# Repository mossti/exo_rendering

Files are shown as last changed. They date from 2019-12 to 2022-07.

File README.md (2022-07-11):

# CABLE-DRIVEN SERIES ELASTIC ACTUATOR FOR UPPER-LIMB REHABILITATIVE EXOSKELETON
*You can see the demo video [here](https://www.youtube.com/watch?v=A_MqyhAG-6s)!*

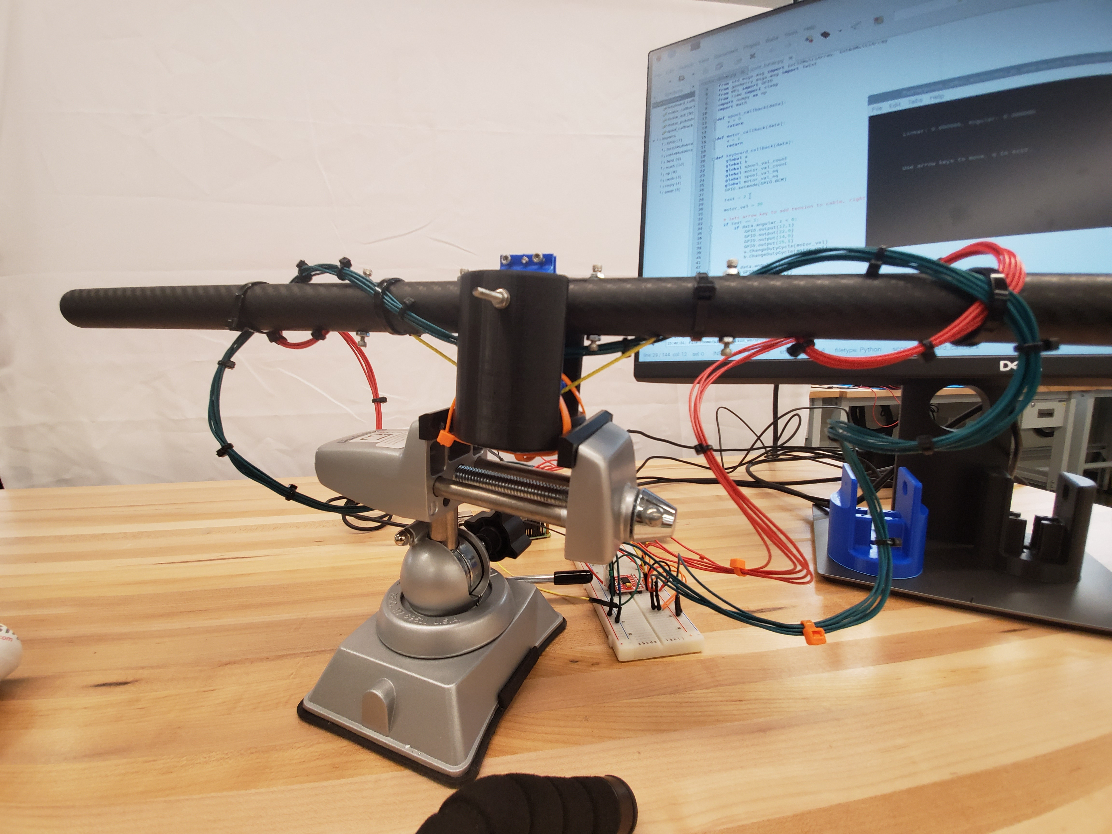
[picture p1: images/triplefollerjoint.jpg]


Individuals effected by a stroke will often develop symptomatic neuromotor control deficits. Depending on the degree of the stroke and the localization in the brain, these deficits can be categorized into impairments of specific neuromotor pathways. Reticulospinal (RS) hyperexcitability is currently believed to be the most likely candidate responsible for a common form of post-stroke spasticity, which can result in weakness and spasmodic motion control in the effected individual. In many cases, motor recovery and reduced spasticity can be achieved through rehabilitative therapy; historically this often takes form via hands-on manipulation and assistance by occupational therapists, repetitive goal-oriented intensive therapy, and medicinal treatments. These therapies, while effective, are often limited in scope by the availability and individual training of medical personnel, the cost of travel and therapy, and difficulties in customizing therapeutic approaches for individual patients.

Ideally, the design of a modular device to facilitate certain aspects common to motor recovery therapies would allow for a greater degree of accessibility to effected populations and more effective and regular training intervals (regularity of training periods is a key factor of successful neurorehabilitation). To this end, we propose a lightweight gravity-balancing exoskeleton with cable-driven elastic actuation, engineered to provide feedback which encourages synergistic patterns of movement that post-stroke spasticity commonly prohibits.

# DESCRIBE EXO; DESCRIBE AND SHOW SEA PROTOTYPES/COMPONENTS
A gravity-balancing machine (in this case, a gravity-balancing orthosis (GBO)) is defined as a mechanical system which can offload the force due to gravity (in part or whole) experienced by a load onto a separate component of the mechanism. In this device, the gravity-balancing subsystem is confined to the upper limbs, allowing for the downward force due to gravity to be offloaded via a series of counterweights (with specific degrees of freedom) onto the user's back. The device is engineered to assist with upper limb neuromotor rehabilitation, and--as such--is concentrated on the minimization of external forces on the upper limbs. Depending on the stage of recovery that a survivor of stroke is currently working through (and concordantly the severity of neuromuscular weakness), the reduction of gravitational forces can greatly reduce the effort/focus required by the user that is dedicated solely to counteracting gravity. Instead, the user's focus can be directed towards the repetitive goal-oriented therapy motions in a manner somewhat analogous to water immersive and equine therapy used for lower-limb rehabilitative approaches. Due to the positioning of the counterweights, the GBO can perform well for a wide range of arm configurations--and can certainly perform well within the range required for the user to engage in therapeutic tasks.

# EXO OVERVIEW
The GBO upper-limb exoskeleton is comprised of a consumer backpack frame (with waist strap for further weight distribution along the user's trunk), and a series of carbon fiber tubes (lightweight, high tensile strength).

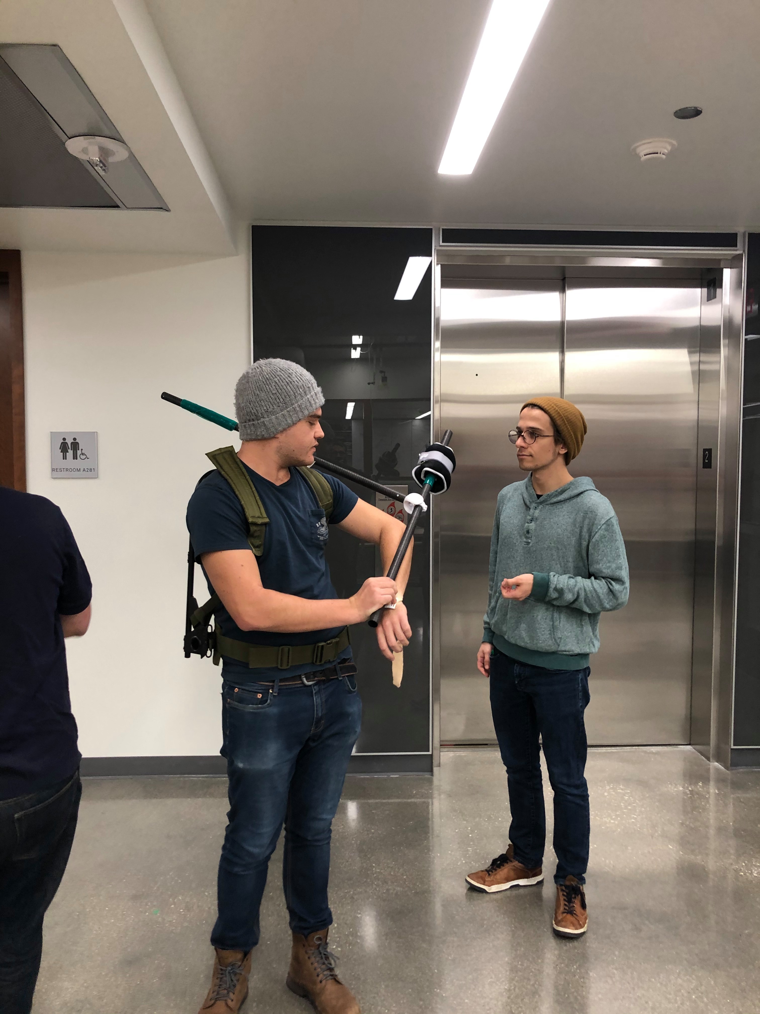
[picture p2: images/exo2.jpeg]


The weights can be adjusted to accommodate different arm lengths and musculature.

# SEA OVERVIEW
A series elastic actuator (SEA) is a form of actuator that inherently supports an elastic component between the actual actuator and the actuator's load. This boasts a number of helpful applications, especially in the domain of rehabilitative/assistive robotics. The elastic component allows for an otherwise rigid robotic system to interact with the environment around it (or a human element) in a non-rigid manner, providing 'give' to the joints. A wonderful caveatthat lends itself well to the realm of rehabilitative robotics is the ability to directly calculate the torque on a joint by tracking the difference in displacement of the motor and load on either side of the elastic component.

# SEA COMPONENTS

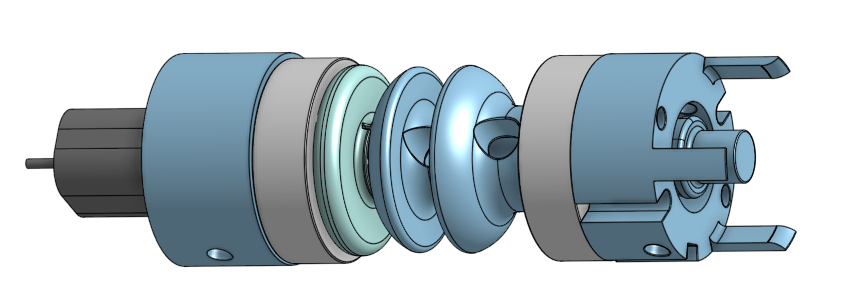
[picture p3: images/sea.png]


## BOM:

* Raspberry Pi 4 Model B (2GB RAM) x1
* Torsion Spring (360 deg, Left-Hand Wound, 0.174''OD) x2
* Ball Bearing (Open, Trade Number R2, for 1/8'' Shaft Diameter) x2
* Carbon Fiber Tube (1" OD, 15/16'' ID, 3ft) x1
* Dyneema Throw Line (MBS: 650lb) x1
* Dycem Non-Slip Material Roll x1
* SunFounder TB6612 H-Bridge x1
* Pololu 250:1 Micro Metal Gearmotor (HP 6V with Extended Motor Shaft) x2
* Pololu Magnetic Encoder Pair Kit for Micro Metal Gearmotors (12 CPR, 2.7-18V) x2
* AEAT-6012 Magnetic Encoder x2
* PLA and Ultimaker 2/3 (or equivalent)

NOTE: A large challenge in this mechanical design is that the assembly was required to fit within a 15/16in carbon fiber tube. Carbon fiber tubing is light, which makes it a strong candidate for exoskeleton scaffolding.

## Assembly

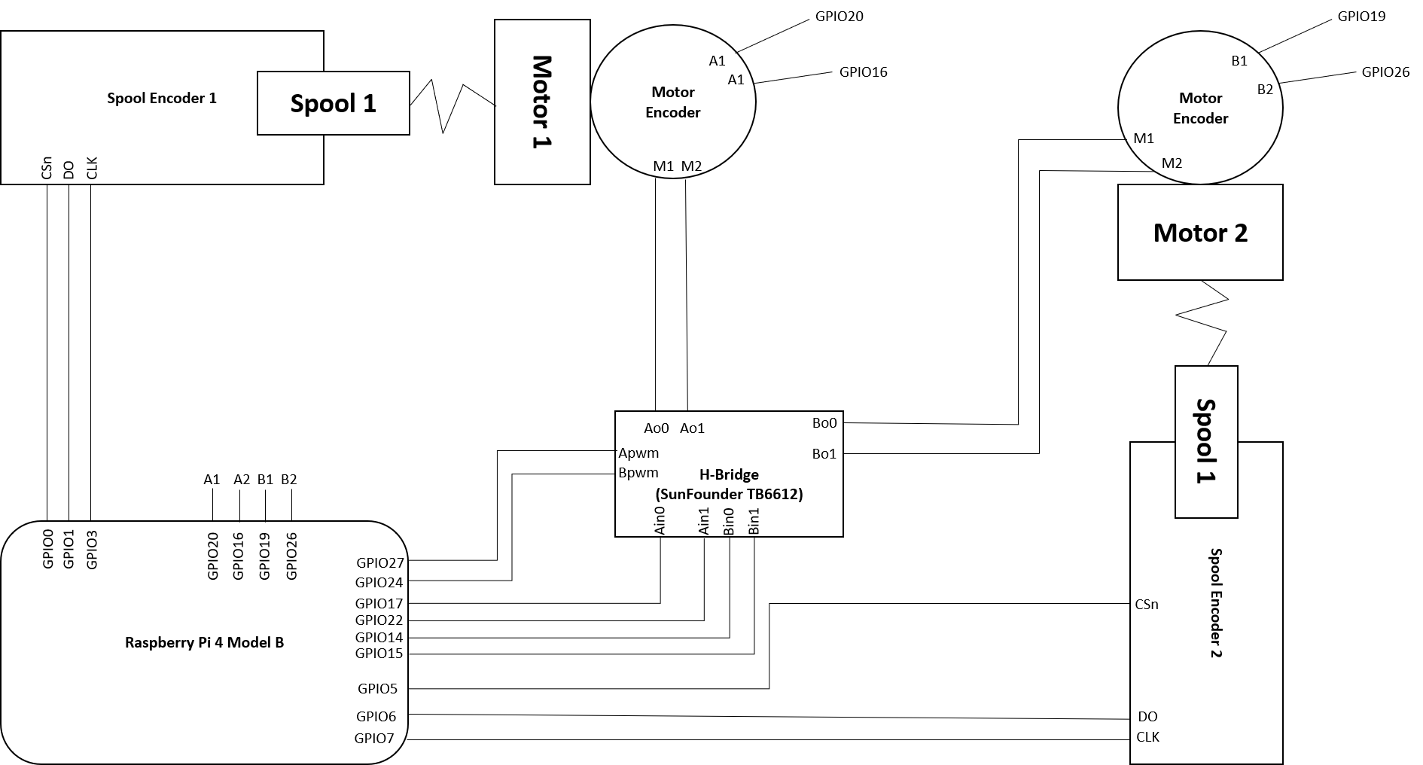
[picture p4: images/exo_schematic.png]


### Motors and motor encoders

The motor encoders are quadrature magnetic encoders attached to the back shaft of the MicroMetal gear motor with 6 counts per revolution (x250 due to gear ratio).

### Spool and spool encoders

The spool encoders are quadrature magnetic encoders with a max resolution of 4095 counters per revolution.

### Spring choice

The requirements for correcting small motions in the GBO are for a relatively low torque actuator that is back-driveable. To achieve this, 250:1 motors were used, connected to low spring constant torsion springs (K = 0.00536 Nm/rev) connected the motors to the spool (e.g., to the load).

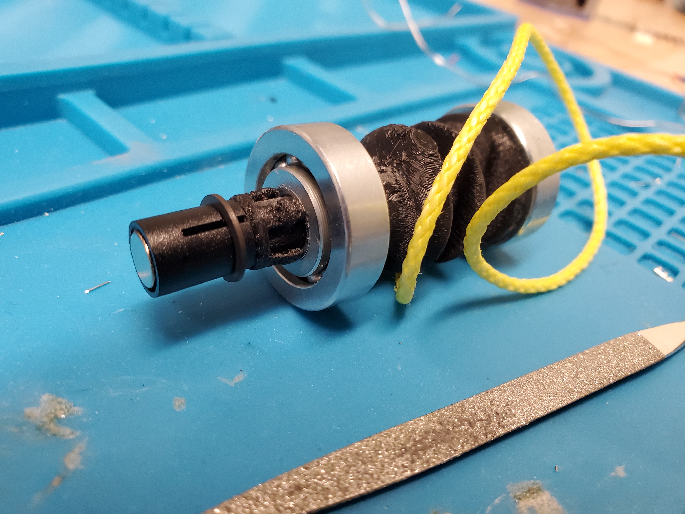
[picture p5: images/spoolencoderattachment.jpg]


# CODE

## ROS information and supporting packages:

This implementation uses:
* ROS Melodic
* catkin, geometry_msgs, roscpp, rospy, std_msgs
* teleop_tools package (for keyboard input tensioning) [get it here](https://github.com/ros-teleop/teleop_tools)!

To use this code, copy the `exo_joint` and the `teleop_tools` packages into your ROS workspace's src folder and run `catkin_make`.

## Pre-tensioning and cable actuation:

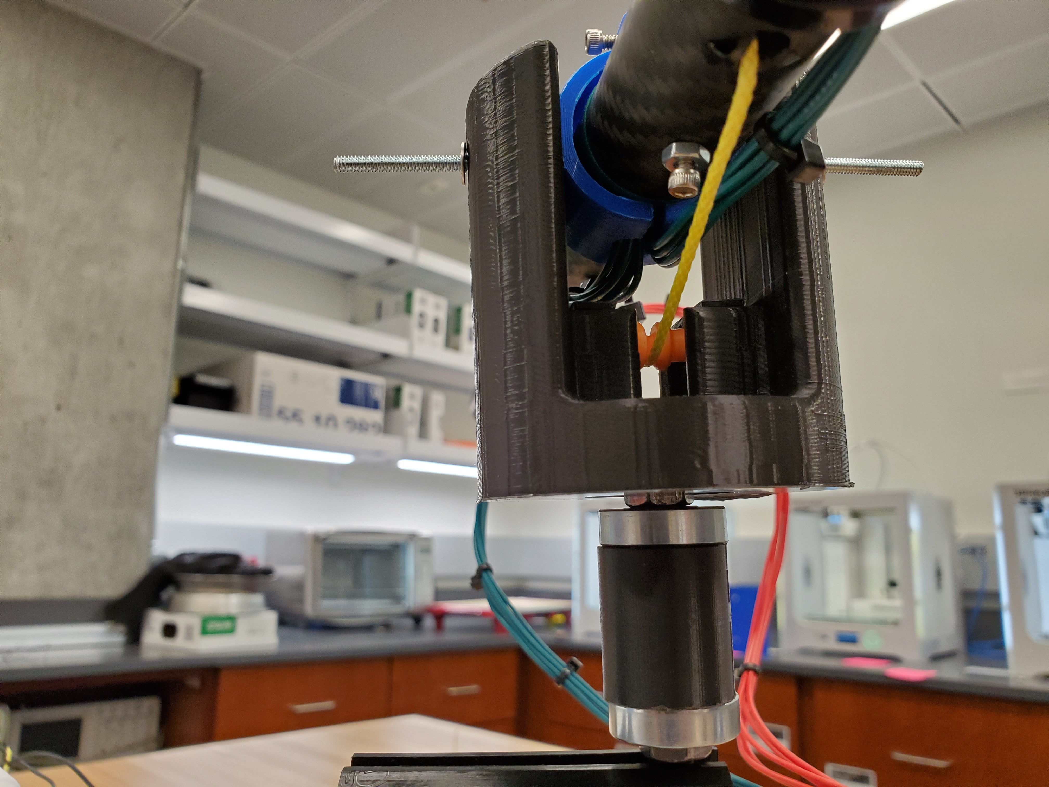
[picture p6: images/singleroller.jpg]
singleroller


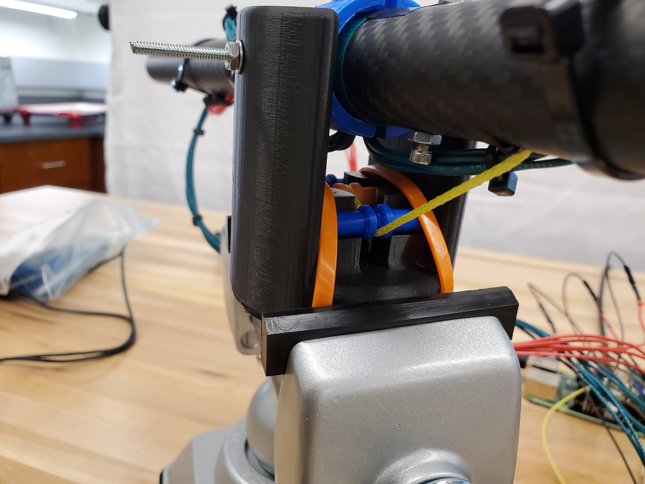
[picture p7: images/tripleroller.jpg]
doubleroller


To pre-tension, use `joint_tuner.py` via `roslaunch exo_joint joint_tuner.py`. Note that this will required `teleop_tools`.

Run `joint_tuner.launch` from the main ROS workspace directory and use the left (motor A CCW, motor B CW) and right (motor A CW, motor B CCW) arrow keys on your keyboard to manually adjust the tension and drive the cable.

## Prevent angular deflection:

The goal with this code (change `test = '1'` in `motor_driver.py`) is to correct small motions, such as those seen in post-stroke spasticity. When the spool encoder begins to increment outside of a threshold range (i.e., when torque is reached), the motor will pull on the spring in the opposite direction via a PID controller to bring the angle back to its original angle.

Run this with `roslaunch exo_joint angle_encoder_test.launch` after changing the value `test` in `motor_callback()` in `motor_driver.py` to `'1'`.

## Follow angular deflection:

The goal with this code (change `test = '2'` in `motor_driver.py`) is to achieve back-driveability. When the spool encoder increments (i.e., when there is sufficient torque on the spring, causing the spool to deflect), the motor fill follow it. This was done using a PID controller.

Run this with `roslaunch exo_joint angle_encoder_test.launch` after changing the value `test` in `motor_callback()` in `motor_driver.py` to `'2'`.

# FUTURE CONSIDERATIONS

One of the largest issues faced was the pre-tensioning of the cable drive. The cable used (Dyneema 650lb throw-line) is extremely low-friction, and using a single roller at ~35 degrees deflection was not enough to cause sufficient tension in the device. Tension is important because it is proportional to the amount of torque across the elastic component at any given time. Low tension means that the spool and motor encoders will behave less like an SEA and more like a conventional actuator with lag. The inclusion of three rollers helped, increasing the tension. This is visible in the demo video.

# CITATIONS

* [1] Agarwal, Priyanshu & Deshpande, Ashish. (2017). Series Elastic Actuators (SEAs) for Small-scale Robotic Applications. Journal of Mechanisms and Robotics. 9. 10.1115/1.4035987.  
* [2] Agarwal, P., Yun, Y., Fox, J., Madden, K., & Deshpande, A. D. (2017). Design, control, and testing of a thumb exoskeleton with series elastic actuation. The International Journal of Robotics Research, 36(3), 355–375. https://doi.org/10.1177/0278364917694428
* [3] F. Huang, R. B. Gillespie and A. Kuo, "Haptic feedback and human performance in a dynamic task," Proceedings 10th Symposium on Haptic Interfaces for Virtual Environment and Teleoperator Systems. HAPTICS 2002, Orlando, FL, USA, 2002, pp. 24-31.
doi: 10.1109/HAPTIC.2002.998937
* [4] Felix C. Huang, R. Brent Gillespie & Arthur D. Kuo (2007) Visual and Haptic Feedback Contribute to Tuning and Online Control During Object Manipulation, Journal of Motor Behavior, 39:3, 179-193, DOI: 10.3200/JMBR.39.3.179-193
* [5] Li S. (2017). Spasticity, Motor Recovery, and Neural Plasticity after Stroke. Frontiers in neurology, 8, 120. doi:10.3389/fneur.2017.00120
* [6] Xu, Y., Terekhov, A. V., Latash, M. L., & Zatsiorsky, V. M. (2012). Forces and moments generated by the human arm: variability and control. Experimental brain research, 223(2), 159–175. doi:10.1007/s00221-012-3235-0

# ACKNOWLEDGEMENTS

Special thanks to the wonderful folks in the MSR 2018-2019 cohort, Dr. Elwin, Dr. Schultz, Billy Strong, and Dr. Huang.

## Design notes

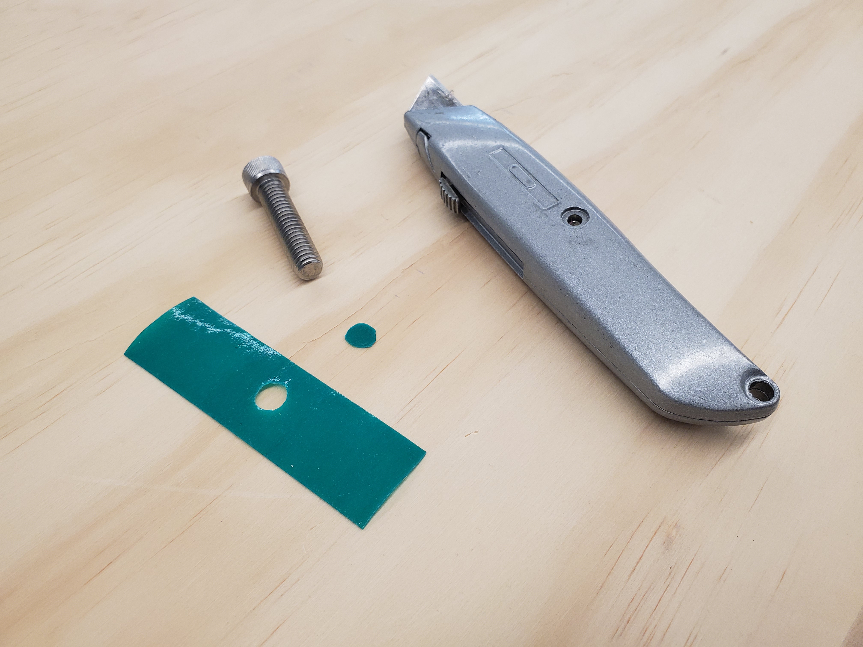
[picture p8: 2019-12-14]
images/dycemgrip.jpg

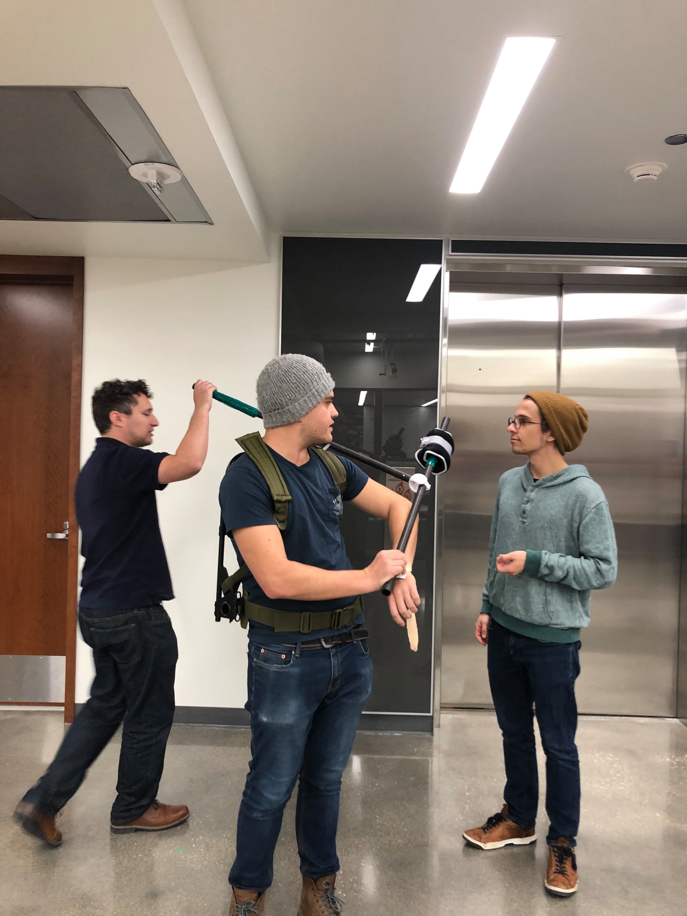
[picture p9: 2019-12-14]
images/exo1.jpeg

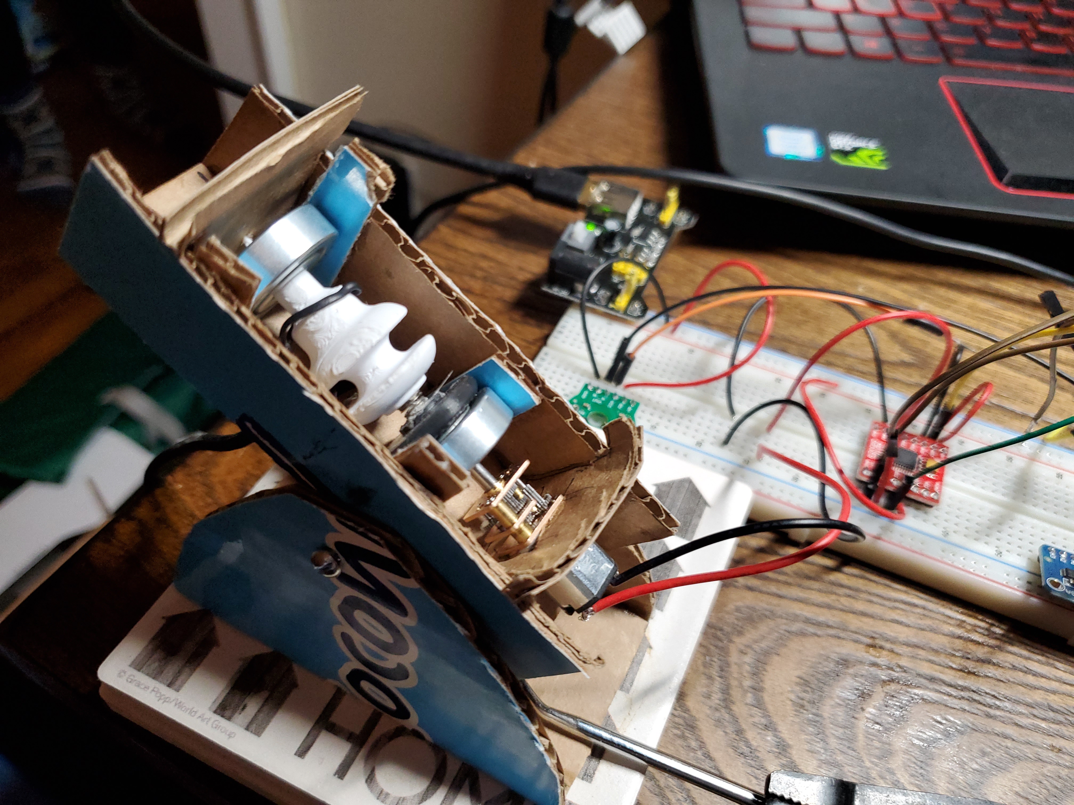
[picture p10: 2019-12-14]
images/gen1.jpg

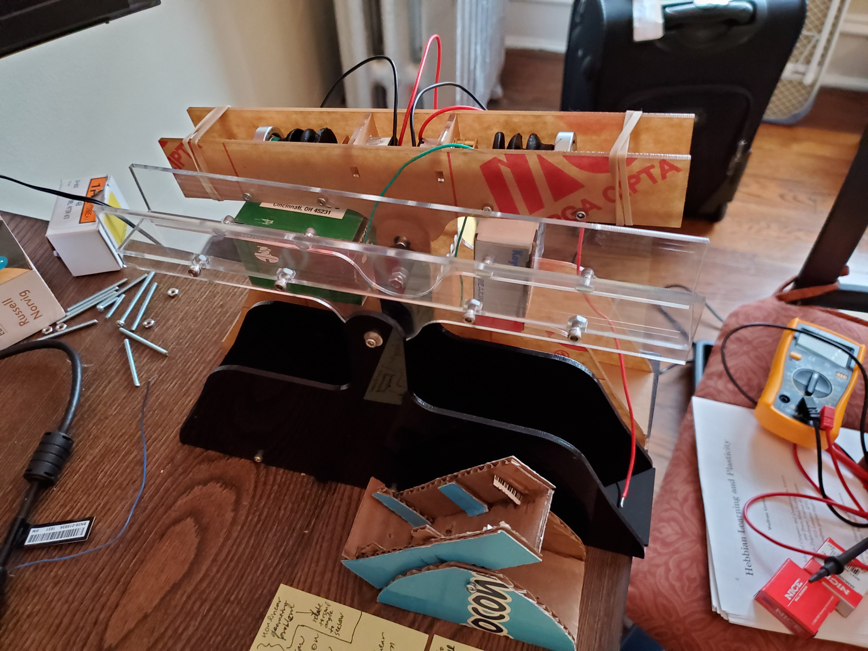
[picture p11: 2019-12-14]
images/threegen.jpg

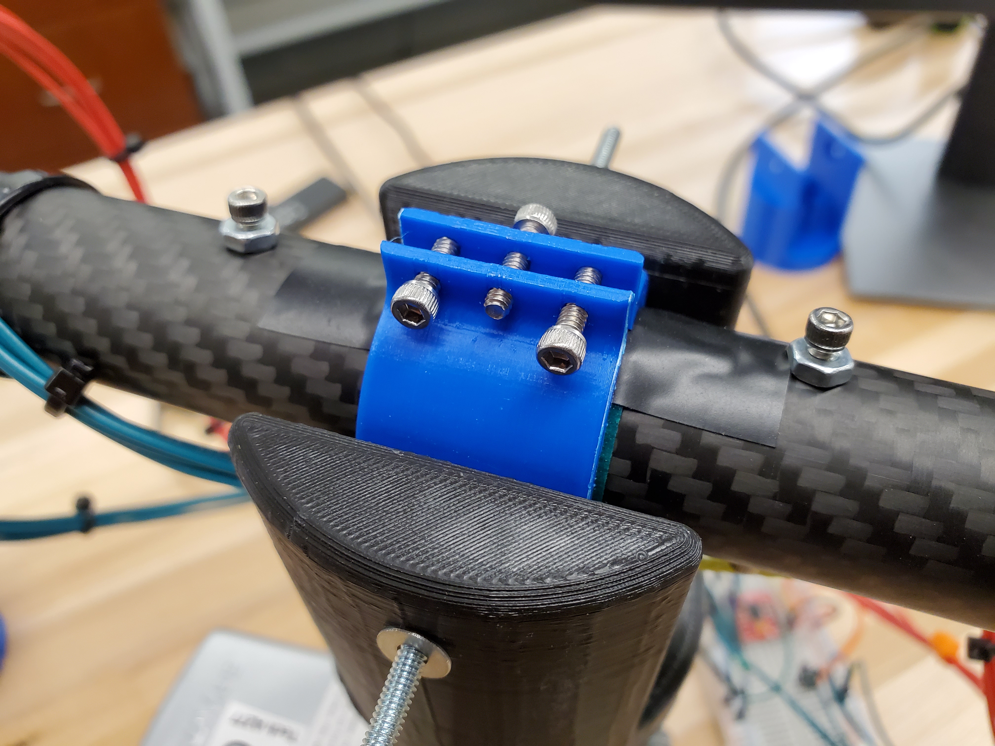
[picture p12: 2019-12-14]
images/adjustableclampwithdycem.jpg

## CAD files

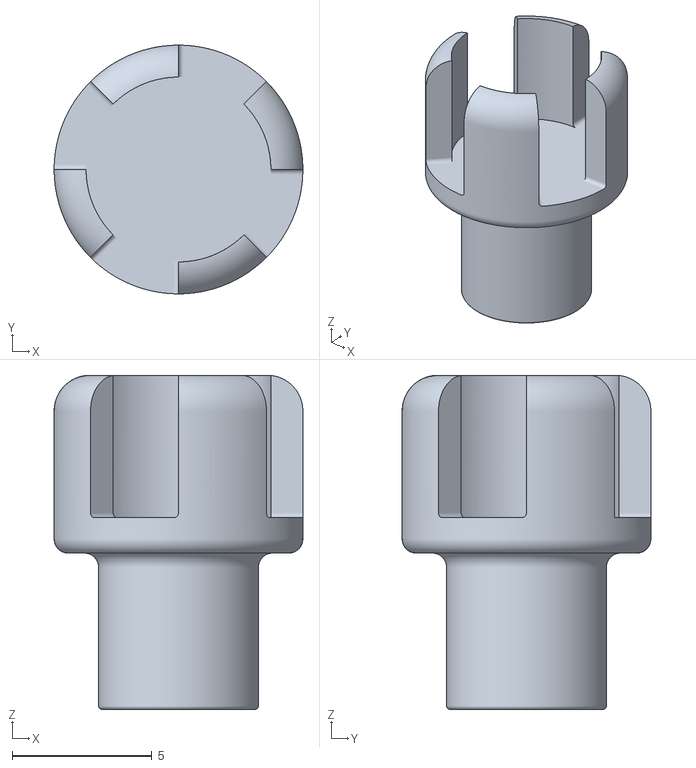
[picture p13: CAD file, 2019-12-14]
stl_files/AEA_magnet_bracket.stl
8.89 x 8.89 x 11.9

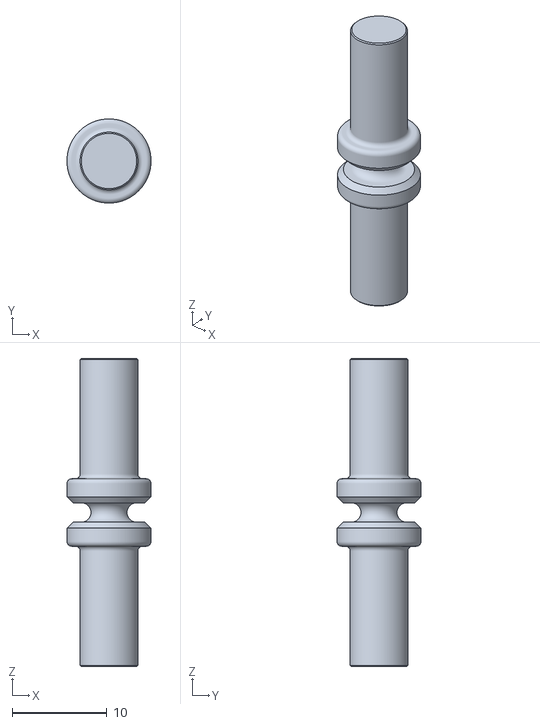
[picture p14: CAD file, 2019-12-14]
stl_files/example_roller_guide.stl
8.89 x 8.89 x 32.5

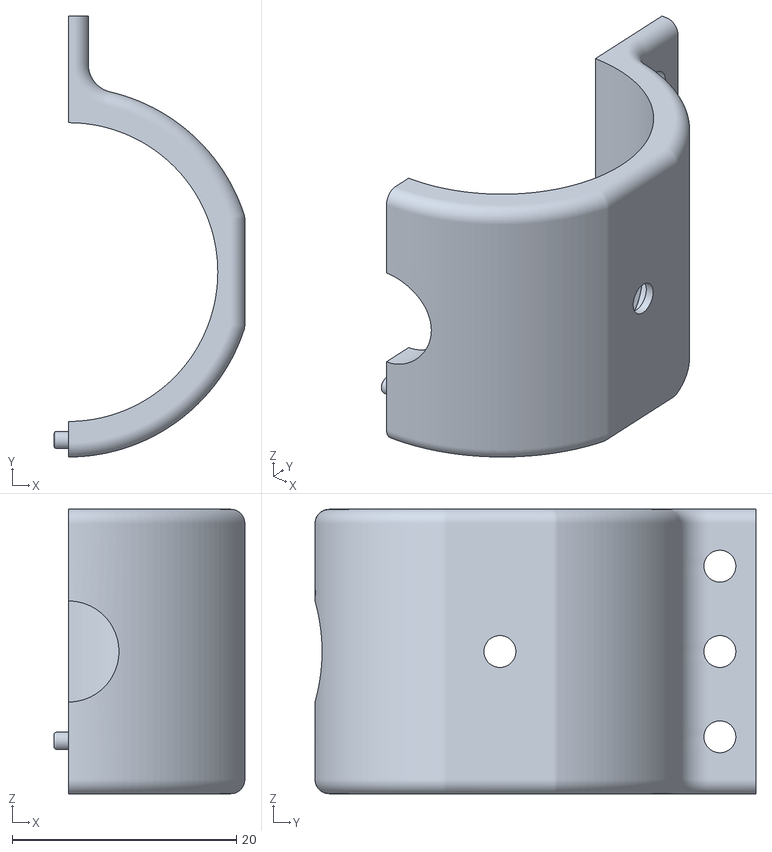
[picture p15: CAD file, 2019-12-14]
stl_files/tube_clamp.stl
17.0 x 39.4 x 25.4

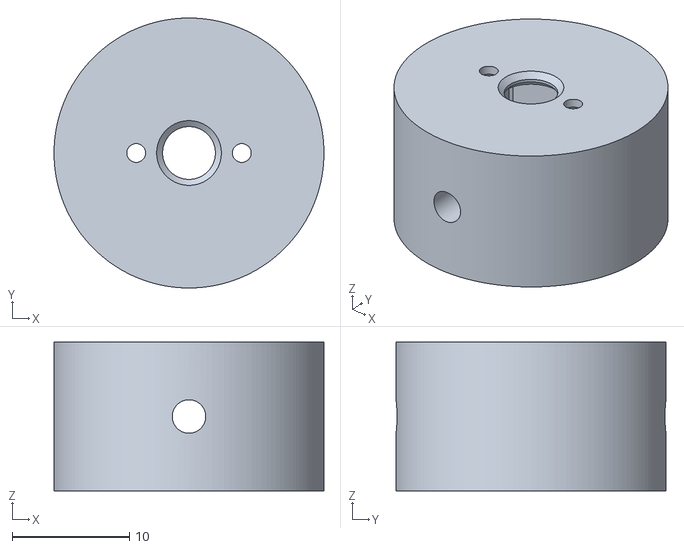
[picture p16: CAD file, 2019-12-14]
stl_files/motor_encoder_bracket.stl
23.0 x 23.0 x 12.7

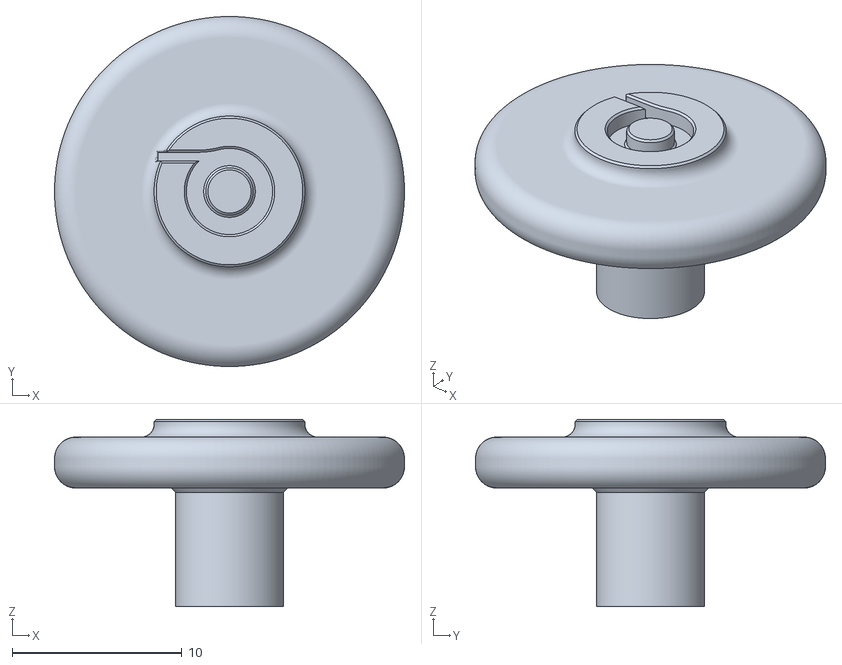
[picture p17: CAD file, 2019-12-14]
stl_files/motor_clamp.stl
20.6 x 20.6 x 11.0

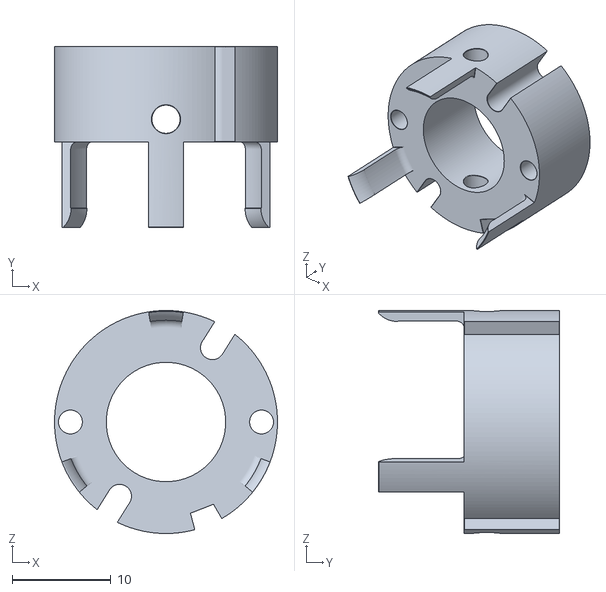
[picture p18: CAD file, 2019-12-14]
stl_files/AEA_encoder_cap.stl
22.6 x 18.3 x 22.6

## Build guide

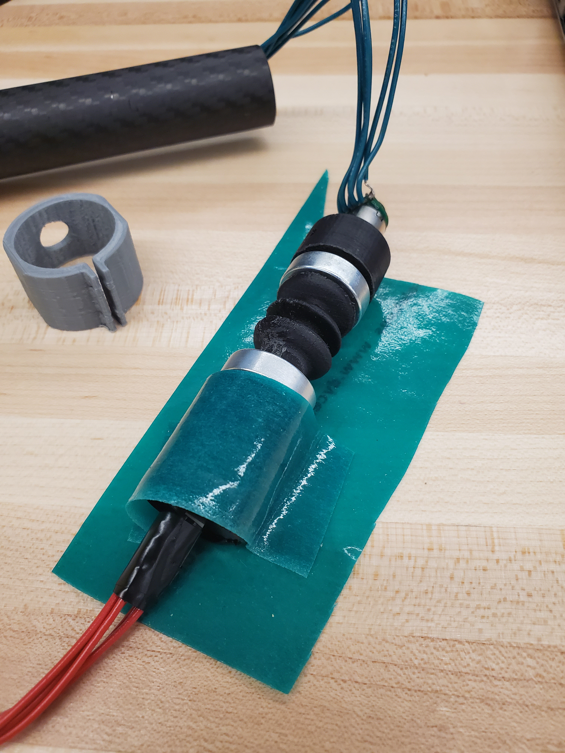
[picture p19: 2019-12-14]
images/assemblytestwithdycem.jpg

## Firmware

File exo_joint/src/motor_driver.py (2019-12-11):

#!/usr/bin/env python

import roslib
import rospy
from std_msgs.msg import Int32MultiArray, Int64MultiArray
from geometry_msgs.msg import Twist
from RPi import GPIO
from time import sleep
import numpy as np
import math

#a = 0
#b = 0
#spool_val_count = 0
#motor_val_count = 0

	#print "*       Modified SunFounder TB6612         *"
	#print "*                                          *"
	#print "*         Connect PWMA to BCM27            *"
	#print "*         Connect Ain1 to BCM17            *"
	#print "*         Connect Ain2 to BCM22            *"
	#print "*         Connect PWMB to BCM24            *"
	#print "*         Connect Bin1 to BCM14            *"
	#print "*         Connect Bin2 to BCM15            *"

def pid_control(delta_theta, int_error, delta_error):
	kp = 1
	ki = 0.01
	kd = 0.01
	vel = kp*delta_theta + ki*int_error + kd*delta_error
	if vel < 0:
		vel = 5
	if vel >= 30:
		vel = 5
	return vel

def motor_init():
	global a
	global b
	global spool_val_count
	global motor_val_count
	global spool_val_eq
	global motor_val_eq
	
	spool_val_count = 0
	motor_val_count = 0
	
	GPIO.setmode(GPIO.BCM)
	GPIO.setup((17,27,22,14,15,24), GPIO.OUT)
	a = GPIO.PWM(27, 60)
	b = GPIO.PWM(24, 60)
	a.start(0)
	b.start(0)
	
	return

def spool_callback(data):
	global a
	global b
	global spool_val_count
	global motor_val_count
	global spool_val_eq
	global motor_val_eq
	global spool_val_a
	global spool_val_b
	global spool_val_init_a
	global spool_val_init_b
	global motor_val_init_a
	global motor_val_init_b
	global spool_val_last_a
	global spool_val_last_b
	global motor_val_last_a
	global motor_val_last_b
	
	global spool_val_high_a
	global spool_val_low_a
	global motor_val_high_a
	global motor_val_low_a
	global spool_val_high_b
	global spool_val_low_b
	global motor_val_high_b
	global motor_val_low_b
	
	global max_deflection
	GPIO.setmode(GPIO.BCM)
	
	if spool_val_count == 0:
		spool_val_eq = data.data
		spool_val_init_a = (float(spool_val_eq[0])/4095)*360 - (float(spool_val_eq[0])/4095)*360
		spool_val_init_b = (float(spool_val_eq[1])/4095)*360 - (float(spool_val_eq[1])/4095)*360
	
	
	
	spool_val_a_mid = ((float(data.data[0] - spool_val_eq[0])/4095)*360)
	spool_val_b_mid = ((float(data.data[1] - spool_val_eq[1])/4095)*360)
	
	if spool_val_a_mid >= 0:
		#spool_val_a = 0 + np.abs((float(data.data[0] - spool_val_eq[0])/4095)*360)
		spool_val_a = 0 + np.abs((float(data.data[0])/4095)*360 - (float(spool_val_eq[0])/4095)*360)
	if spool_val_a_mid < 0:
		#spool_val_a = 360 - np.abs((float(data.data[0] - spool_val_eq[0])/4095)*360)
		spool_val_a = 360 - np.abs((float(data.data[0])/4095)*360 - (float(spool_val_eq[0])/4095)*360)
		
	
	if spool_val_b_mid >= 0:
		spool_val_b = 0 + np.abs((float(data.data[1])/4095)*360 - (float(spool_val_eq[1])/4095)*360)
	if spool_val_b_mid < 0:
		spool_val_b = 360 - np.abs((float(data.data[1])/4095)*360 - (float(spool_val_eq[1])/4095)*360)
	
	#rospy.loginfo(rospy.get_caller_id() + " | spool_val_a: " + str(int(spool_val_init_a)) + "/" + str(int(spool_val_a)) + " | spool_val_b: " + str(int(spool_val_init_b)) + "/" + str(int(spool_val_b)))
	#rospy.loginfo(rospy.get_caller_id() + "spool_val_b: " + str(spool_val_b))
	#rospy.loginfo(rospy.get_caller_id() + " | " + str(int(((360-spool_val_init_a) - (360-spool_val_a)))) + " | " + str(int(((360-spool_val_init_b) - (360-spool_val_b)))))
	
	#if ((360-spool_val_init_a) - (360-spool_val_a)) >= 100:
	#if (spool_val_a >= (spool_val_init_a + 180)):
	#	if np.abs(spool_val_init_a - (360-spool_val_a)) >= 100:
	#		if 360-spool_val_a > (spool_val_init_a):
	#			GPIO.output(17,1)
	#			GPIO.output(22,0)
	#			a.ChangeDutyCycle(15)
	#		if 360-spool_val_a < (spool_val_init_a):
	#			GPIO.output(17,0)
	#			GPIO.output(22,1)
	#			a.ChangeDutyCycle(15)
				
	#if (spool_val_a < (spool_val_init_a + 180)):
	#	if np.abs(spool_val_init_a - (360-spool_val_a)) >= 100:
	#		if 360-spool_val_a > spool_val_init_a:
	#			GPIO.output(17,0)
	#			GPIO.output(22,1)
	#			a.ChangeDutyCycle(15)
	#		if 360-spool_val_a < spool_val_init_a:
	#			GPIO.output(17,1)
	#			GPIO.output(22,0)
	#			a.ChangeDutyCycle(15)
				
	#if (spool_val_b >= (spool_val_init_b + 180)):			
	#	if np.abs(spool_val_init_b - (360-spool_val_b)) >= 100:
	#		if 360-spool_val_a > spool_val_init_b:
	#			GPIO.output(14,0)
	#			GPIO.output(15,1)
	#			b.ChangeDutyCycle(15)
	#		if 360-spool_val_a < spool_val_init_b:
	#			GPIO.output(14,1)
	#			GPIO.output(15,0)
	#			b.ChangeDutyCycle(15)
	
	
	#if (spool_val_b < (spool_val_init_b + 180)):
	#	if np.abs(spool_val_init_b - (360-spool_val_b)) >= 100:
	#		if 360-spool_val_a > spool_val_init_b:
	#			GPIO.output(14,1)
	#			GPIO.output(15,0)
	#			b.ChangeDutyCycle(15)
	#		if 360-spool_val_a < spool_val_init_b:
	#			GPIO.output(14,0)
	#			GPIO.output(15,1)
	#			b.ChangeDutyCycle(15)
			
	
	#if np.abs(spool_val_a-spool_val_init_a) < 100:
	#	a.ChangeDutyCycle(0)
	
	#if np.abs(spool_val_b-spool_val_init_b) < 100:
	#	b.ChangeDutyCycle(0)	
	
	
	spool_val_count += 1
	spool_val_last_a = spool_val_a
	spool_val_last_b = spool_val_b
	return

def motor_callback(data):
	global a
	global b
	global spool_val_count
	global motor_val_count
	global spool_val_eq
	global motor_val_eq
	global spool_val_a
	global spool_val_b
	global spool_val_init_a
	global spool_val_init_b
	global motor_val_init_a
	global motor_val_init_b
	global spool_val_last_a
	global spool_val_last_b
	global motor_val_last_a
	global motor_val_last_b
	global spool_val_a_track
	global spool_val_b_track
	
	global spool_val_high_a
	global spool_val_low_a
	global motor_val_high_a
	global motor_val_low_a
	global spool_val_high_b
	global spool_val_low_b
	global motor_val_high_b
	global motor_val_low_b
	
	global dist_a
	global dist_b
	global dist_a_last
	global dist_b_last
	
	global delta_a
	global delta_b
	global int_delta_a
	global int_delta_b
	
	global flag_a
	global flag_b
	
	global turn_tracker_a
	global turn_tracker_b
	
	global test
	global high_val
	global mid_val
	
	global max_deflection
	GPIO.setmode(GPIO.BCM)
		
	if motor_val_count == 0:
		
		motor_val_eq = data.data
		spool_val_a = 0
		spool_val_b = 0
		spool_val_last_a = 0
		spool_val_last_b = 0
		motor_val_last_a = 0
		motor_val_last_b = 0
		spool_val_a_track = 0
		spool_val_b_track = 0
		motor_val_a_track = 0
		motor_val_b_track = 0
		
		spool_val_high_a = 0
		spool_val_low_a = 0
		motor_val_high_a = 0
		motor_val_low_a = 0
		spool_val_high_b = 0
		spool_val_low_b = 0
		motor_val_high_b = 0
		motor_val_low_b = 0
		
		dist_a = 0
		dist_b = 0
		dist_a_last = dist_a
		dist_b_last = dist_b
		
		delta_a = 0
		delta_b = 0
		int_delta_a = 0
		int_delta_b = 0
		
		flag_a = '...'
		flag_b = '...'
		turn_tracker_a = 0
		turn_tracker_b = 0
		
		test = '2'
		high_val = 360
		mid_val = high_val/2
		max_deflection = high_val/18
	
	#motor_val_a = ((float(data.data[0] - motor_val_eq[0])/248.98)*360)%360
	#motor_val_b = ((float(data.data[1] - motor_val_eq[1])/248.98)*360)%360
	motor_val_a = ((float(data.data[0] - motor_val_eq[0])/248.98)*high_val)%high_val
	motor_val_b = ((float(data.data[1] - motor_val_eq[1])/248.98)*high_val)%high_val
	
	#rospy.loginfo(str(dist_a))
	#rospy.loginfo(str(dist_b))
	#rospy.loginfo(str(dist_a_last))
	#rospy.loginfo(str(dist_b_last))
	#rospy.loginfo(str(delta_a))
	#rospy.loginfo(str(delta_b))
	#rospy.loginfo(str(int_delta_a))
	#rospy.loginfo(str(int_delta_b))
	
	#rospy.loginfo(rospy.get_caller_id() + " | " + "motor_val_a: " + str(int(motor_val_eq[0])) + "/" + str(int(motor_val_a)) + " | " + "motor_val_b: " + str(int(motor_val_eq[1])) + "/" + str(int(motor_val_b)))
	#rospy.loginfo(rospy.get_caller_id() + "motor_val_b: " + str(motor_val_b))
	
	#rospy.loginfo(str(int(motor_val_a)) + "/" + str(int(spool_val_a)) + " | " + str(int(motor_val_b)) + "/" + str(int(spool_val_b)))
	#rospy.loginfo(str(int(spool_val_a%360 - motor_val_a%360)) + " | " + str(int(spool_val_b%360 - motor_val_b%360)))
	#rospy.loginfo(str(int(spool_val_a - (360-motor_val_a))) + " | " + str(int(spool_val_b - (360-motor_val_b))))
	#rospy.loginfo(str(int(np.abs(spool_val_a - (360-motor_val_a)))) + " | " + str(int(np.abs(spool_val_b - (360-motor_val_b)))))
	
	#rospy.loginfo(str(int(motor_val_a-motor_val_last_a)) + " | " + str(int(spool_val_a-spool_val_last_a)))
	
	#rospy.loginfo(str(int(spool_val_a)) + " | " + str(int(spool_val_a_track)) + "    ...    " + str(int(np.abs(motor_val_a - spool_val_a_track))) + "/" + str(int(max_deflection)) + " || " + str(int(spool_val_b)) + " | " + str(int(spool_val_b_track)) + "    ...    " + str(int(np.abs(motor_val_b - spool_val_b_track))) + "/" + str(int(max_deflection)))
	
	
	### PID VELOCITY CONTROL TERMS
	delta_a = dist_a_last - dist_a
	delta_b = dist_b_last - dist_b
	
	int_delta_a += delta_a
	int_delta_b += delta_b
	
	motor_v_a = pid_control(dist_a, int_delta_a, delta_a)
	motor_v_b = pid_control(dist_b, int_delta_b, delta_b)
	
	#motor_v_a = 15
	#motor_v_b = 15
	
	
	
	if (motor_val_last_a > 0 and motor_val_last_a < mid_val) and (motor_val_a > mid_val):
		turn_tracker_a -= 1
	
	if (motor_val_last_a > mid_val) and (motor_val_a > 0 and motor_val_a < mid_val):
		turn_tracker_a +=1
	
	if (motor_val_last_b > 0 and motor_val_last_b < mid_val) and (motor_val_b > mid_val):
		turn_tracker_b -= 1
	
	if (motor_val_last_b > mid_val) and (motor_val_b > 0 and motor_val_b < mid_val):
		turn_tracker_b +=1
	
	spool_val_low_a = 0 + spool_val_a
	spool_val_high_a = high_val - spool_val_a
	motor_val_low_a = 0 + motor_val_a
	motor_val_high_a = high_val - motor_val_a
	
	spool_val_low_b = 0 + spool_val_b
	spool_val_high_b = high_val - spool_val_b
	motor_val_low_b = 0 + motor_val_b
	motor_val_high_b = high_val - motor_val_b
	
	# MOTOR CORRECTS ELASTIC DEVIATION CASE; TEST = '1'
	if test == '1':
	
		if spool_val_a > motor_val_a:
			dist_low_a = spool_val_high_a + motor_val_low_a
			dist_high_a = spool_val_a - motor_val_a
			if dist_low_a < dist_high_a:
				dist_a = dist_low_a
				if dist_a > max_deflection:
					#rospy.loginfo("SVA > MVA ; DIST_LOW < DIST_HIGH ; DIST A > MAX DEFLECTION")
					GPIO.output(17,0)
					GPIO.output(22,1)
					a.ChangeDutyCycle(motor_v_a)
					flag_a = "-->"
			if dist_high_a < dist_low_a:
				dist_a = dist_high_a
				if dist_a > max_deflection:
					#rospy.loginfo("SVA > MVA ; DIST_LOW > DIST_HIGH ; DIST A > MAX DEFLECTION")
					GPIO.output(17,1)
					GPIO.output(22,0)
					a.ChangeDutyCycle(motor_v_a)
					flag_a = "<--"
				
		if spool_val_a < motor_val_a:
			dist_low_a = spool_val_low_a + motor_val_high_a
			dist_high_a = motor_val_a - spool_val_a
			if dist_low_a < dist_high_a:
				dist_a = dist_low_a
				if dist_a > max_deflection:
					#rospy.loginfo("SVA < MVA ; DIST_LOW < DIST_HIGH ; DIST A > MAX DEFLECTION")
					GPIO.output(17,0)
					GPIO.output(22,1)
					flag_a = "-->"
					a.ChangeDutyCycle(motor_v_a)
			if dist_high_a < dist_low_a:
				dist_a = dist_high_a
				if dist_a > max_deflection:
					#rospy.loginfo("SVA < MVA ; DIST_LOW > DIST_HIGH ; DIST A > MAX DEFLECTION")
					GPIO.output(17,1)
					GPIO.output(22,0)
					a.ChangeDutyCycle(motor_v_a)
					flag_a = "<--"
					
		if spool_val_b > motor_val_b:
			dist_low_b = spool_val_high_b + motor_val_low_b
			dist_high_b = spool_val_b - motor_val_b
			if dist_low_b < dist_high_b:
				dist_b = dist_low_b
				if dist_b > max_deflection:
					#rospy.loginfo("SVB > MVB ; DIST_LOW < DIST_HIGH ; DIST B > MAX DEFLECTION")
					GPIO.output(14,1)
					GPIO.output(15,0)
					b.ChangeDutyCycle(motor_v_b)
					flag_b = "-->"
			if dist_high_b < dist_low_b:
				dist_b = dist_high_b
				if dist_b > max_deflection:
					#rospy.loginfo("SVB > MVB ; DIST_LOW > DIST_HIGH ; DIST B > MAX DEFLECTION")
					GPIO.output(14,0)
					GPIO.output(15,1)
					b.ChangeDutyCycle(motor_v_b)
					flag_b = "<--"
					
		if spool_val_b < motor_val_b:
			dist_low_b = spool_val_low_b + motor_val_high_b
			dist_high_b = motor_val_b - spool_val_b
			if dist_low_b < dist_high_b:
				dist_b = dist_low_b
				if dist_b > max_deflection:
					#rospy.loginfo("SVB < MVB ; DIST_LOW < DIST_HIGH ; DIST B > MAX DEFLECTION")
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

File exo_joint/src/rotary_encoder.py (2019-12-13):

from RPi import GPIO
from time import sleep

clk2 = 19 #B1
clk1 = 20 #A1
dt2 = 26 #B2
dt1 = 16 #A2

GPIO.setmode(GPIO.BCM)
GPIO.setup(clk1, GPIO.IN, pull_up_down=GPIO.PUD_DOWN)
GPIO.setup(clk2, GPIO.IN, pull_up_down=GPIO.PUD_DOWN)
GPIO.setup(dt1, GPIO.IN, pull_up_down=GPIO.PUD_DOWN)
GPIO.setup(dt2, GPIO.IN, pull_up_down=GPIO.PUD_DOWN)

counter1 = 0
counter2 = 0
clkLastState1 = GPIO.input(clk1)
clkLastState2 = GPIO.input(clk2)

try:

        while True:
                clkState1 = GPIO.input(clk1)
                clkState2 = GPIO.input(clk2)
                dtState1 = GPIO.input(dt1)
                dtState2 = GPIO.input(dt2)
                if clkState1 != clkLastState1:
                        if dtState1 != clkState1:
                                counter1 += 1
                        else:
                                counter1 -= 1
                        print counter1
                        
                if clkState2 != clkLastState2:
                        if dtState2 != clkState2:
                                counter2 += 1
                        else:
                                counter2 -= 1
                        print counter2
                        
                clkLastState1 = clkState1
                clkLastState2 = clkState2
                sleep(0.01)
finally:
        GPIO.cleanup()
        
if __name__ == '__main__':
	try:
		main()
	except KeyboardInterrupt:
		k = 1
                GPIO.cleanup()
		destroy()

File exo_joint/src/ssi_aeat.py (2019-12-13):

import time
import numpy as np
import RPi.GPIO as GPIO

# Three-wire SSI for AEAT-601012
# (#1) CS = 0, DO = 1, CLK = 3
# (#2) CS = 5, DO = 6, CLK = 7

def ssi_init():
	GPIO.output(0,1)
	GPIO.output(3,1)
	GPIO.output(5,1)
	GPIO.output(7,1)

def start_read():
	GPIO.output(0,0)
	GPIO.output(5,0)
	a = GPIO.input(1)
	b = GPIO.input(6)
	print(a)
	print(b)
	time.sleep(0.0000001)
	a = GPIO.input(1)
	b = GPIO.input(6)
	print(a)
	print(b)
	time.sleep(0.0000004)
	a = GPIO.input(1)
	b = GPIO.input(6)
	print(a)
	print(b)
	GPIO.output(3,0)
	GPIO.output(7,0)
	a = GPIO.input(1)
	b = GPIO.input(6)
	print(a)
	print(b)
	return

def main():
	import time
	global k
	k = 0
	
	GPIO.setmode(GPIO.BCM)
	GPIO.setup((0,3), GPIO.OUT)
	GPIO.setup((5,7), GPIO.OUT)
	GPIO.setup(1,GPIO.IN)
	GPIO.setup(6,GPIO.IN)
	
	ssi_init()
	
	time.sleep(0.2)
	
	while k != 1: 
		entry = np.array([0])
		
		ssi_init()
		
		time.sleep(0.0000005)
		
		start_read()
		
		time.sleep(5/1000000.0)
		
		for i in range(0,12):
			
			GPIO.output(3,1)
			GPIO.output(7,1)
			
			time.sleep(0.000000375)
			
			a = GPIO.input(1)
			b = GPIO.input(6)
			
			time.sleep(0.000000125)
			
			GPIO.output(3,0)
			GPIO.output(7,0)
			
			time.sleep(0.0000005)
			
			if i == 0:
				#entry[0] = a
				entry_a = str(a)
				entry_b = str(b)
			else:
				#entry = np.append(entry, a)
				entry_a = entry_a + str(a)
				entry_b = entry_b + str(b)
				
			
		#entry = np.array2string(entry)
		entry_a = int(entry_a,2)
		entry_b = int(entry_b,2)
		
		print(entry_a)
		print(entry_b)
	
	return
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
